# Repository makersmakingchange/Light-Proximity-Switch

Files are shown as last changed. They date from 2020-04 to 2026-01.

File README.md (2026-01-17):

# Light Proximity Switch

> [!IMPORTANT]
2026-Jan-16 Several of the electronic components in this design are no longer available. We are working to determine suitable replacements.

The Light Proximity Switch is an open-source assistive switch that is activated by movement or extremely light contact. It can be activated by waving a hand or limb over the device. This switch has an output cable with a standard 3.5 mm plug and it can be used to control a variety of switch-adapted devices including phones, computers, adapted toys, and gaming consoles.

The Light Proximity Switch is comprised of off-the-shelf electronics, a custom printed circuit board (PCB), and 3D printed parts.

The Light Proximity Switch is open assistive technology (OpenAT). Under the terms of the open source licenses, the device may be built, used, and improved by anyone.

The overall cost of materials for a single build is approximately $35 CAD.

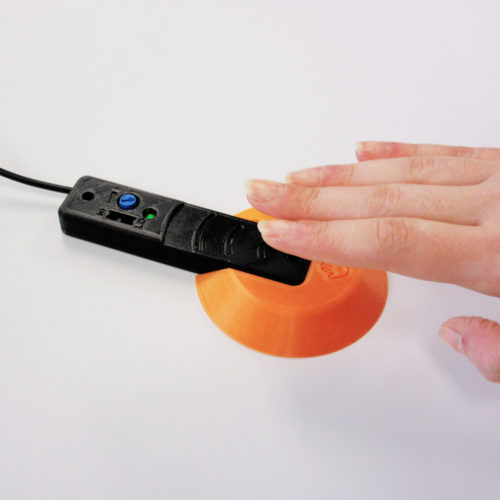
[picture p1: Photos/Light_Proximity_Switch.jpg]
A hand hovering over a black Light Proximity Switch with an orange base.


## More info at

- [Makers Making Change Library Page](https://www.makersmakingchange.com/s/product/light-proximity-switch/01tJR0000006942YAA)

## Usage
Plug the 3.5 mm cable from the switch into the device you want to control. Wave a hand or limb over the sensor to trigger the device (the green LED should light up). 

Fine tune the motion sensitivity by toggling the black switch to "HI" or "LO" then fine tuning using the blue dial.

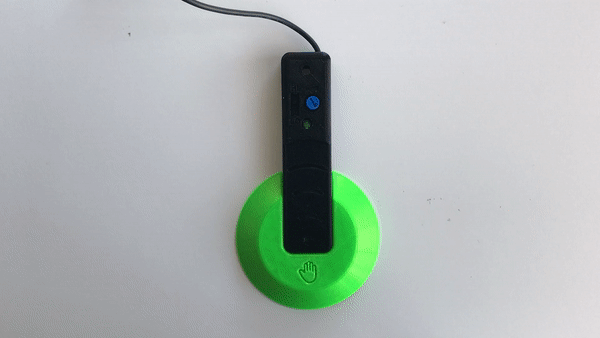
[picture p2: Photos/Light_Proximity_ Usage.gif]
An animation showing the the green light on the Light Proximity Switch activating as a hand is passed over the sensor.


To attach the 3D printed circular base, simply slide the base onto the switch until it clicks into place. This may take a bit of force. The inclined surface of the can make it easier for a user to push their hand up to activate the sensor.

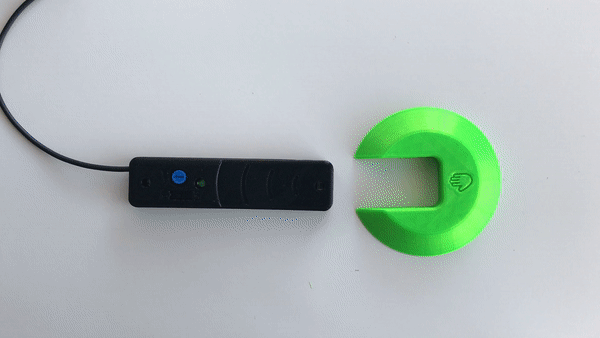
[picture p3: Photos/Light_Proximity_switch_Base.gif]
An animation showing the circular base being clipped on to the Light Proximity Switch.


## How to Obtain the Device
### 1. Do-it-Yourself (DIY) or Do-it-Together (DIT)

This is an open-source assistive technology, so anyone is free to build it. All of the files and instructions required to build the device are contained within this repository. Refer to the documentation below.

### 2. Request a build of this device

You may also submit a build request through the [MMC Library Page](https://www.makersmakingchange.com/s/product/light-proximity-switch/01tJR0000006942YAA) to have a volunteer maker build the device. As the requestor, you are responsible for reimbursing the maker for the cost of materials and any shipping.

### 3. Build this device for someone else

If you have the skills and equipment to build this device, and would like to donate your time to create the device for someone who needs it, visit the [MMC Maker Wanted](https://makersmakingchange.com/maker-wanted/) section.

## Build Instructions

### 1. Read through the Documentation

<!--- The [Assembly Guide](/Documentation/Light_Proxity_Switch_Makery_Guide.pdf) contains all the necessary information to build this device, including tool lists, assembly instructions, and testing. --->
Read through the documentation below.

### 2. Order the Custom Printed Circuit Board (PCB)

This device requires a custom PCB. It will need to be ordered from a PCB fabrication service. The Gerber files can be found in the [PCB Build Files](/Build_Files/PCB_Build_Files/). 

### 3. Order the Off-The-Shelf Components

The [Bill of Materials](/Documentation/Light_Proximity_Switch_BOM.csv) lists all of the parts and components required to build the device. This build also requires a custom PCB.

### 4. Print the 3D Printable components

All of the individual print files can be found in the [/Build_Files/3D_Printing_Files](/Build_Files/3D_Printing/) folder.

### 5. Assemble the Light Proximity Switch

Reference the [Assembly Guide](/Documentation/Light_Proxity_Switch_Assembly_Guide.pdf) for the tools and steps required to build each portion.

## How to improve this Device Design
As open assistive technology, you are welcomed and encouraged to improve upon the design. 

## Files
### Documentation
| Document             | Version | Link |
|----------------------|---------|------|
| Design Rationale     | n/a     | WIP   |
| Bill of Materials    | 1.0     |  [Light Proximity Switch BOM](/Documentation/Light_Proximity_Switch_BOM.csv)  |
| Tool List | 1.0 | [Light Proximity Switch Tools List](/Documentation/Light_Proximity_Switch_Tools_List.pdf)|
| Assembly Guide       | 1.0     | [Light Proximity Switch Assembly Guide](/Documentation/Light_Proxity_Switch_Assembly_Guide.pdf) |
| QC Quide | 1.0 | [Light Proximity Switch QC Guide](/Documentation/Light_Proximity_Switch_QC_Guide.pdf)|
| Troubleshooting Guide | 1.0 | [Light Proximity Switch Troubleshooting Guide](/Documentation/Light_Proximity_Switch_Troubleshooting_Guide.pdf)|
| Delivery Checklist | 1.0 | [Light Proximity Delivery Checklist](/Documentation/Light_Proximity_Switch_Delivery_Checklist.pdf)|
| User Guide           | 1.0     | [Light Proximity Switch User Guide](/Documentation/Light_Proximity_Switch_User_Guide.pdf) |
| Changelog            | n/a     | -     |

### Design Files
<!---
DESIGN FILES
--->
 - [CAD Files](/Design_Files/CAD_Design_Files)
 - [PCB Design Files](/Design_Files/PCB_Design_Files/)

### Build Files
 - [3D Printing Files](/Build_Files/3D_Printing_Files)
 - [PCB Build Files](/Build_Files/PCB_Build_Files)

## License
Copyright (c) 2019-2026 Neil Squire / Makers Making Change.

This repository describes Open Hardware:
 - Everything needed or used to design, make, test, or prepare the Light Proximity Switch is licensed under the [CERN 2.0 Weakly Reciprocal license (CERN-OHL-W v2) or later](https://cern.ch/cern-ohl ) .
 - Accompanying material such as instruction manuals, videos, and other copyrightable works that are useful but not necessary to design, make, test, or prepare the Light Proximity Switch are published under a [Creative Commons Attribution-ShareAlike 4.0 license (CC BY-SA 4.0)](https://creativecommons.org/licenses/by-sa/4.0/) .

You may redistribute and modify this documentation and make products using it under the terms of the [CERN-OHL-W v2](https://cern.ch/cern-ohl).
This documentation is distributed WITHOUT ANY EXPRESS OR IMPLIED WARRANTY, INCLUDING OF MERCHANTABILITY, SATISFACTORY QUALITY AND FITNESS FOR A PARTICULAR PURPOSE.
Please see the CERN-OHL-W v2 for applicable conditions.

Source Location: https://github.com/makersmakingchange/Light-Proximity-Switch

## Attribution
The Light Proximity Switch is an original design by Neil Squire / Maker Making Change Program.

### Contributors
  - Derrick Andrews, Neil Squire Society / Makers Making Change.
  - Jake McIvor, Neil Squire Society / Makers Making Change.
  - Kristina Mok, Neil Squire Society / Makers Making Change.

<!-- ABOUT MMC START -->
## About Makers Making Change
[Makers Making Change Logo](https://www.makersmakingchange.com/)

Makers Making Change is a program of [Neil Squire](https://www.neilsquire.ca/), a Canadian non-profit that uses technology, knowledge, and passion to empower people with disabilities.

Makers Making Change leverages the capacity of community based Makers, Disability Professionals and Volunteers to develop and deliver affordable Open Source Assistive Technologies.

 - Website: [www.MakersMakingChange.com](https://www.makersmakingchange.com/)
 - GitHub: [makersmakingchange](https://github.com/makersmakingchange)
 - Bluesky: [@makersmakingchange.bsky.social](https://bsky.app/profile/makersmakingchange.bsky.social)
 - Instagram: [@makersmakingchange](https://www.instagram.com/makersmakingchange)
 - Facebook: [makersmakechange](https://www.facebook.com/makersmakechange)
 - LinkedIn: [Neil Squire Society](https://www.linkedin.com/company/neil-squire-society/)
 - Thingiverse: [makersmakingchange](https://www.thingiverse.com/makersmakingchange/about)
 - Printables: [MakersMakingChange](https://www.printables.com/@MakersMakingChange)

### Contact Us
For technical questions, to get involved, or to share your experience we encourage you to [visit our website](https://www.makersmakingchange.com/) or [contact us](https://www.makersmakingchange.com/s/contact).
<!-- ABOUT MMC END -->

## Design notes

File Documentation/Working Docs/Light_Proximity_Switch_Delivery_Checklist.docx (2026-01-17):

## Maker To Do

Light Proximity Switch - Device Delivery Checklist

☐ Build the Light Proximity Switch

☐ 3D print the switch base

# Items for the User

☐ Light Proximity Switch

☐ Light Proximity Switch Base

☐ Light Proximity Switch: User Guide

Neil Squire, 2020 © 2020 by Neil Squire. Proximity Switch Delivery Checklist is made available under a Creative Commons Attribution-ShareAlike 4.0 License (International): http://creativecommons.org/licenses/by-sa/4.0

Version 1.0 | March 2020 www.MakersMakingChange.com

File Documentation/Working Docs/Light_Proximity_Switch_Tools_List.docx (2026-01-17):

Proximity Switch: Tool List

# Tools

- Soldering iron
- Solder
- Flush cutters
- Wire strippers
- Needle nose pliers
- Mini Philips screwdriver
- De-soldering tool
- Tape
- Clamp

Neil Squire, 2020 © 2020 by Neil Squire. Proximity Switch Tool List is made available under a Creative Commons Attribution-ShareAlike 4.0 License (International): http://creativecommons.org/licenses/by-sa/4.0

Version 1.0 | February 2020 www.MakersMakingChange.com

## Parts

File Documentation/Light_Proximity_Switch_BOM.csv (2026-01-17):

Qty | Component | Component name | Supplier | Manufacturer | MPN | Digi-Key Part Number | Unit Cost (CAD) | Build Cost (CAD) | Link
1 | IC1 | IC OPAMP GP 1 CIRCUIT 8DIP | DigiKey | Microchip Technology | MCP6231-E/P | MCP6231-E/P-ND | $0.69 | $0.69 | https://www.digikey.ca/en/products/detail/microchip-technology/MCP6231-E-P/716239?s=N4IgTCBcDaILIGEAKA2MBmAjAWgKIHolsA5AERAF0BfIA
2 | D1,D3 | SENSOR PHOTODIODE 850NM 2DIP | DigiKey | OSRAM | BPW34 | 475-1070-ND | $1.63 | $3.26 | https://www.digikey.ca/product-detail/en/osram-opto-semiconductors-inc/BPW34/475-1070-ND/607274
1 | D2 | Schottky diode 1N5817 | DigiKey | STMicroelectronics | 1N5817 | 497-4547-1-ND | $0.33 | $0.33 | https://www.digikey.ca/en/products/detail/stmicroelectronics/1N5817/770963
1 | LED1 | LED GREEN CLEAR 5MM ROUND | DigiKey | Cree LED | C566D-GFF-CY14Q7S1 | C566D-GFF-CY14Q7S1-ND | $0.43 | $0.43 | https://www.digikey.ca/en/products/detail/cree-led/C566D-GFF-CY14Q7S1/4793750
1 | C1 | CAP CER 10000PF 50V Z5U RADIAL | DigiKey | KEMET | C315C103M5U5TA7301 | 399-13973-1-ND | $0.40 | $0.40 | https://www.digikey.ca/product-detail/en/kemet/C315C103M5U5TA7301/399-13973-1-ND/6562544
2 | C2,C5 | CAP CER 33PF 50V X7R RADIAL | DigiKey | KEMET | C315C330K2G5TA7301 | 399-13940-1-ND | $0.54 | $1.08 | https://www.digikey.ca/product-detail/en/kemet/C315C330K2G5TA7301/399-13940-1-ND/6562533
1 | C3 | CAP CER 10PF 50V C0G/NP0 RADIAL | DigiKey | Vishay Siliconix | K100J15C0GF5TL2 | BC1001CT-ND | $0.35 | $0.35 | https://www.digikey.ca/product-detail/en/vishay-bc-components/K100J15C0GF5TL2/BC1001CT-ND/286623
1 | C4 | CAP CER 1UF 25V X7R RADIAL | DigiKey | KEMET | C315C105K3R5TA | 399-9714-ND | $1.32 | $1.32 | https://www.digikey.ca/en/products/detail/kemet/C315C105K3R5TA/3726118
1 | R1 | TRIMMER 100K OHM 0.5W PC PIN TOP | DigiKey | Bourns Inc. | 3386P-1-104TLF | 3386P-104TLF-ND | $3.39 | $3.39 | https://www.digikey.ca/product-detail/en/bourns-inc/3386P-1-104TLF/3386P-104TLF-ND/1232548
1 | R3 | 200K Resistor | DigiKey | Yageo | CFR-25JB-52-200K | 200KQBK-ND | $0.15 | $0.15 | https://www.digikey.ca/product-detail/en/yageo/CFR-25JB-52-200K/200KQBK-ND/711
1 | R2 | RES 10K OHM 1/4W 5% AXIAL | DigiKey | Yageo | CFR-25JB-52-10K | 10KQBK-ND | $0.15 | $0.15 | https://www.digikey.ca/product-detail/en/yageo/CFR-25JB-52-10K/10KQBK-ND/338
1 | B1 | CR2032 battery holder | DigiKey | Memory Protection Devices | BU2032SM-BT-GTR | BU2032SM-FH-GCT-ND | $1.88 | $1.88 | https://www.digikey.ca/en/products/detail/mpd-memory-protection-devices/BU2032SM-BT-GTR/2439521
1 | S1 | SWITCH SLIDE SPDT 200MA 30V | DigiKey | E-Switch | EG1218 | EG1903-ND | $1.21 | $1.21 | https://www.digikey.ca/product-detail/en/e-switch/EG1218/EG1903-ND/101726
1 | 3.5mm Cable | CBL ASSY 3.5MM SLIM 6' MONO BLK | DigiKey | Tensility International Corp | 10-00344 | 839-1039-ND | $3.49 | $3.49 | https://www.digikey.ca/product-detail/en/tensility-international-corp/10-00344/839-1039-ND/2350247
1 | Cable Tie | Cable Tie, Nylon, 71 mm long, 1.8 mm wide | Digikey | Panduit | PLT.6SM-C | PLT.6SM-C | $0.32 | $0.32 | https://www.digikey.ca/en/products/detail/panduit-corp/PLT-6SM-C/280029
2 | Screws | M2X8mm screw | DigiKey | APM Hexseal | RM2X8MM 2701 | 335-1155-ND | $1.14 | $2.28 | https://www.digikey.ca/product-detail/en/apm-hexseal/RM2X8MM-2701/335-1155-ND/612919
2 | Q1,Q2 | MOSFET N-CH 100V 1A 4-DIP | Amazon |  | IRLD110PBF |  | $1.28 | $2.55 | https://www.amazon.ca/10PCS-IRLD110-DIP4-IRLD110PBF-DIP-4/dp/B0DSSJTPH8
1 | CR2032 | CR2032 3V Battery | Amazon | AmazonBasics | CR2032 |  | $0.73 | $0.73 | https://www.amazon.ca/AmazonBasics-Lithium-CR2032-Batteries-10-Pack/dp/B07RXJ4S7Z
 |  |  |  |  |  | Total Electronics Cost | $24.01 | $24.01

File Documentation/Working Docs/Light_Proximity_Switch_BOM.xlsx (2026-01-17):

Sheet: Electronics
Qty | Component | Component name | Supplier | Manufacturer | MPN | Digi-Key Part Number | Unit Cost (CAD) | Build Cost (CAD) | Link
1 | IC1 | IC OPAMP GP 1 CIRCUIT 8DIP | DigiKey | Microchip Technology | MCP6231-E/P | MCP6231-E/P-ND | $0.69 | $0.69 | https://www.digikey.ca/en/products/detail/microchip-technology/MCP6231-E-P/716239?s=N4IgTCBcDaILIGEAKA2MBmAjAWgKIHolsA5AERAF0BfIA
2 | D1,D3 | SENSOR PHOTODIODE 850NM 2DIP | DigiKey | OSRAM | BPW34 | 475-1070-ND | $1.63 | $3.26 | https://www.digikey.ca/product-detail/en/osram-opto-semiconductors-inc/BPW34/475-1070-ND/607274
1 | D2 | Schottky diode 1N5817 | DigiKey | STMicroelectronics | 1N5817 | 497-4547-1-ND | $0.33 | $0.33 | https://www.digikey.ca/en/products/detail/stmicroelectronics/1N5817/770963
1 | LED1 | LED GREEN CLEAR 5MM ROUND | DigiKey | Cree LED | C566D-GFF-CY14Q7S1 | C566D-GFF-CY14Q7S1-ND | $0.43 | $0.43 | https://www.digikey.ca/en/products/detail/cree-led/C566D-GFF-CY14Q7S1/4793750
1 | C1 | CAP CER 10000PF 50V Z5U RADIAL | DigiKey | KEMET | C315C103M5U5TA7301 | 399-13973-1-ND | $0.40 | $0.40 | https://www.digikey.ca/product-detail/en/kemet/C315C103M5U5TA7301/399-13973-1-ND/6562544
2 | C2,C5 | CAP CER 33PF 50V X7R RADIAL | DigiKey | KEMET | C315C330K2G5TA7301 | 399-13940-1-ND | $0.54 | $1.08 | https://www.digikey.ca/product-detail/en/kemet/C315C330K2G5TA7301/399-13940-1-ND/6562533
1 | C3 | CAP CER 10PF 50V C0G/NP0 RADIAL | DigiKey | Vishay Siliconix | K100J15C0GF5TL2 | BC1001CT-ND | $0.35 | $0.35 | https://www.digikey.ca/product-detail/en/vishay-bc-components/K100J15C0GF5TL2/BC1001CT-ND/286623
1 | C4 | CAP CER 1UF 25V X7R RADIAL | DigiKey | KEMET | C315C105K3R5TA | 399-9714-ND | $1.32 | $1.32 | https://www.digikey.ca/en/products/detail/kemet/C315C105K3R5TA/3726118
1 | R1 | TRIMMER 100K OHM 0.5W PC PIN TOP | DigiKey | Bourns Inc. | 3386P-1-104TLF | 3386P-104TLF-ND | $3.39 | $3.39 | https://www.digikey.ca/product-detail/en/bourns-inc/3386P-1-104TLF/3386P-104TLF-ND/1232548
1 | R3 | 200K Resistor | DigiKey | Yageo | CFR-25JB-52-200K | 200KQBK-ND | $0.15 | $0.15 | https://www.digikey.ca/product-detail/en/yageo/CFR-25JB-52-200K/200KQBK-ND/711
1 | R2 | RES 10K OHM 1/4W 5% AXIAL | DigiKey | Yageo | CFR-25JB-52-10K | 10KQBK-ND | $0.15 | $0.15 | https://www.digikey.ca/product-detail/en/yageo/CFR-25JB-52-10K/10KQBK-ND/338
1 | B1 | CR2032 battery holder | DigiKey | Memory Protection Devices | BU2032SM-BT-GTR | BU2032SM-FH-GCT-ND | $1.88 | $1.88 | https://www.digikey.ca/en/products/detail/mpd-memory-protection-devices/BU2032SM-BT-GTR/2439521
1 | S1 | SWITCH SLIDE SPDT 200MA 30V | DigiKey | E-Switch | EG1218 | EG1903-ND | $1.21 | $1.21 | https://www.digikey.ca/product-detail/en/e-switch/EG1218/EG1903-ND/101726
1 | 3.5mm Cable | CBL ASSY 3.5MM SLIM 6' MONO BLK | DigiKey | Tensility International Corp | 10-00344 | 839-1039-ND | $3.49 | $3.49 | https://www.digikey.ca/product-detail/en/tensility-international-corp/10-00344/839-1039-ND/2350247
1 | Cable Tie | Cable Tie, Nylon, 71 mm long, 1.8 mm wide | Digikey | Panduit | PLT.6SM-C | PLT.6SM-C | $0.32 | $0.32 | https://www.digikey.ca/en/products/detail/panduit-corp/PLT-6SM-C/280029
2 | Screws | M2X8mm screw | DigiKey | APM Hexseal | RM2X8MM 2701 | 335-1155-ND | $1.14 | $2.28 | https://www.digikey.ca/product-detail/en/apm-hexseal/RM2X8MM-2701/335-1155-ND/612919
2 | Q1,Q2 | MOSFET N-CH 100V 1A 4-DIP | Amazon |  | IRLD110PBF |  | $1.28 | $2.55 | https://www.amazon.ca/10PCS-IRLD110-DIP4-IRLD110PBF-DIP-4/dp/B0DSSJTPH8
1 | CR2032 | CR2032 3V Battery | Amazon | AmazonBasics | CR2032 |  | $0.73 | $0.73 | https://www.amazon.ca/AmazonBasics-Lithium-CR2032-Batteries-10-Pack/dp/B07RXJ4S7Z
 |  |  |  |  |  | Total Electronics Cost | $24.01 | $24.01

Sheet: PCB
Qty | Manufacturer | Fabrication Time | Delivery option | Delivery Cost (USD) | Fabrication Cost(USD) | Tax (USD) | Total Cost (USD) | Total Cost (CAD) | Unit Cost (CAD) | Link
5 | JLCPCB | 1-2 days for green and 3-4 for other colors | *S.F Express( 3-5 business days) | $24.82 | $2 | $15.00 | $41.82 | $55.62 | $11.12 | https://jlcpcb.com
5 | JLCPCB | 1-2 days for green and 3-4 for other colors | *DHL Express ( 3-5 business days) | $20.22 | $2 | $15.00 | $37.22 | $49.50 | $9.90 | https://jlcpcb.com
5 | JLCPCB | 1-2 days for green and 3-4 for other colors | Registered Air Mail (15-20 business days) | $9.47 | $2 | $0.00 | $11.47 | $15.26 | $3.05 | https://jlcpcb.com
10 | JLCPCB | 3-4 days for green and 5-6 for other colors | *S.F Express( 3-5 business days) | $24.82 | $5 | $15.00 | $44.82 | $59.61 | $5.96 | https://jlcpcb.com
10 | JLCPCB | 3-4 days for green and 5-6 for other colors | *DHL Express ( 3-5 business days) | $20.22 | $5 | $15.00 | $40.22 | $53.49 | $5.35 | https://jlcpcb.com
10 | JLCPCB | 3-4 days for green and 5-6 for other colors | Registered Air Mail (15-20 business days) | $9.47 | $5 | $0.00 | $14.47 | $19.25 | $1.92 | https://jlcpcb.com
50 | JLCPCB | 5-6 days for green | *S.F Express( 3-5 business days) | $24.82 | $12.80 | $15.00 | $52.62 | $69.98 | $1.40 | https://jlcpcb.com
50 | JLCPCB | 7-8 for other colors | *S.F Express( 3-5 business days) | $24.82 | $27.30 | $15.00 | $67.12 | $89.27 | $1.79 | https://jlcpcb.com
50 | JLCPCB | 5-6 days for green | *DHL Express ( 3-5 business days) | $20.22 | $12.80 | $15.00 | $48.02 | $63.87 | $1.28 | https://jlcpcb.com
50 | JLCPCB | 7-8 for other colors | *DHL Express ( 3-5 business days) | $20.22 | $27.30 | $15.00 | $62.52 | $83.15 | $1.66 | https://jlcpcb.com
50 | JLCPCB | 5-6 days for green | Registered Air Mail (15-20 business days) | $13.29 | $12.80 | $0.00 | $26.09 | $34.70 | $0.69 | https://jlcpcb.com
50 | JLCPCB | 7-8 for other colors | Registered Air Mail (15-20 business days) | $13.29 | $27.30 | $0.00 | $40.59 | $53.98 | $1.08 | https://jlcpcb.com
5 | PCBWay | 1-2 days for green and 3-4 for other colors | *DHL Express ( 3-5 business days) | $21 | $5 | $15.00 | $41.00 | $54.53 | $10.91 | https://www.pcbway.com/
5 | PCBWay | 1-2 days for green and 3-4 for other colors | China Post ( 10-15 business days) | $7 | $5 | $0.00 | $12.00 | $15.96 | $3.19 | https://www.pcbway.com/
5 | PCBWay | 1-2 days for green and 3-4 for other colors | E-packet ( 25-40 business days) | $6 | $5 | $0.00 | $11.00 | $14.63 | $2.93 | https://www.pcbway.com/
5 | PCBWay | 1-2 days for green and 3-4 for other colors | *FedEx IE (6-10 business days) | $26 | $5 | $15.00 | $46.00 | $61.18 | $12.24 | https://www.pcbway.com/
10 | PCBWay | 1-2 days for green and 3-4 for other colors | *DHL Express ( 3-5 business days) | $21 | $5 | $15.00 | $41.00 | $54.53 | $5.45 | https://www.pcbway.com/
10 | PCBWay | 1-2 days for green and 3-4 for other colors | E-packet ( 10-15 business days) | $7 | $5 | $0.00 | $12.00 | $15.96 | $1.60 | https://www.pcbway.com/
10 | PCBWay | 1-2 days for green and 3-4 for other colors | China Post ( 25-40 business days) | $7 | $5 | $0.00 | $12.00 | $15.96 | $1.60 | https://www.pcbway.com/
10 | PCBWay | 1-2 days for green and 3-4 for other colors | *FedEx IE (6-10 business days) | $26 | $5 | $15.00 | $46.00 | $61.18 | $6.12 | https://www.pcbway.com/
50 | PCBWay | 1-2 days for green and 3-4 for other colors | *DHL Express ( 3-5 business days) | $28 | $27 | $15.00 | $70.00 | $93.10 | $1.86 | https://www.pcbway.com/
50 | PCBWay | 1-2 days for green and 3-4 for other colors | E-packet ( 10-15 business days) | $11 | $27 | $0.00 | $38.00 | $50.54 | $1.01 | https://www.pcbway.com/
50 | PCBWay | 1-2 days for green and 3-4 for other colors | China Post ( 25-40 business days) | $11 | $27 | $0.00 | $38.00 | $50.54 | $1.01 | https://www.pcbway.com/
50 | PCBWay | 1-2 days for green and 3-4 for other colors | *FedEx IE (6-10 business days) | $26 | $27 | $15.00 | $68.00 | $90.44 | $1.81 | https://www.pcbway.com/
5 | SeeedStudio Fusion | 3-4 for all colors (2 more days for Matte Black ) | *DHL ( 1-3 business days) | $23.8 | $4.9 | $15.00 | $43.70 | $58.12 | $11.62 | https://www.seeedstudio.com
5 | SeeedStudio Fusion | 3-4 for all colors (2 more days for Matte Black ) | *FedEx (4-8 business days) | $24.55 | $4.9 | $15.00 | $44.45 | $59.12 | $11.82 | https://www.seeedstudio.com
10 | SeeedStudio Fusion | 3-4 for all colors (2 more days for Matte Black ) | *DHL ( 1-3 business days) | $23.8 | $4.9 | $15.00 | $43.70 | $58.12 | $5.81 | https://www.seeedstudio.com
10 | SeeedStudio Fusion | 3-4 for all colors (2 more days for Matte Black ) | *FedEx (4-8 business days) | $24.55 | $4.9 | $15.00 | $44.45 | $59.12 | $5.91 | https://www.seeedstudio.com
50 | SeeedStudio Fusion | 3-4 for all colors (2 more days for Matte Black ) | *DHL ( 1-3 business days) | $26.70 | $26.36 | $15.00 | $68.06 | $90.52 | $1.81 | https://www.seeedstudio.com
50 | SeeedStudio Fusion | 3-4 for all colors (2 more days for Matte Black ) | *FedEx (4-8 business days) | $28.54 | $26.36 | $15.00 | $69.90 | $92.97 | $1.86 | https://www.seeedstudio.com
100 | SeeedStudio Fusion | 3-4 for all colors (2 more days for Matte Black ) | *DHL ( 1-3 business days) | $29.60 | $39.13 | $15.00 | $83.73 | $111.36 | $1.11 | https://www.seeedstudio.com
100 | SeeedStudio Fusion | 3-4 for all colors (2 more days for Matte Black ) | *FedEx (4-8 business days) | $32.50 | $39.13 | $15.00 | $86.63 | $115.22 | $1.15 | https://www.seeedstudio.com
3 | OSH Park | Prototype (9-12 business days) [1] |  |  | $15.85 |  |  |  |  | https://oshpark.com/
6 | OSH Park | Prototype (9-12 business days) [1] |  |  | $31.7 |  |  |  |  | https://oshpark.com/
9 | OSH Park | Prototype (9-12 business days) [1] |  |  | $47.55 |  |  |  |  | https://oshpark.com/
12 | OSH Park | Prototype (9-12 business days) [1] |  |  | $63.40 |  |  |  |  | https://oshpark.com/
21 | OSH Park | Prototype (9-12 business days) [1] |  |  | $110.95 |  |  |  |  | https://oshpark.com/
51 | OSH Park | Prototype (9-12 business days) [1] |  |  | $269.45 |  |  |  |  | https://oshpark.com/
102 | OSH Park | Prototype (9-12 business days) [1] |  |  | $538.90 |  |  |  |  | https://oshpark.com/
3 | OSH Park | Super Swift (4-5 business days) [2] |  |  | $31.70 |  |  |  |  | https://oshpark.com/
6 | OSH Park | Super Swift (4-5 business days) [2] |  |  | $63.40 |  |  |  |  | https://oshpark.com/
9 | OSH Park | Super Swift (4-5 business days) [2] |  |  | $95.1 |  |  |  |  | https://oshpark.com/
12 | OSH Park | Super Swift (4-5 business days) [2] |  |  | $126.80 |  |  |  |  | https://oshpark.com/
21 | OSH Park | Super Swift (4-5 business days) [2] |  |  | $221.90 |  |  |  |  | https://oshpark.com/
51 | OSH Park | Super Swift (4-5 business days) [2] |  |  | $538.90 |  |  |  |  | https://oshpark.com/
102 | OSH Park | Super Swift (4-5 business days) [2] |  |  | $1077.80 |  |  |  |  | https://oshpark.com/
40 | OSH Park | Bulk Order (9-14 business days) [3] |  |  | $126.80 |  |  |  |  | https://oshpark.com/
50 | OSH Park | Bulk Order (9-14 business days) [3] |  |  | $158.50 |  |  |  |  | https://oshpark.com/
100 | OSH Park | Bulk Order (9-14 business days) [3] | Standard First Class Mail(5-21 business days) | $0 | $317 | $0 | $317.00 | $421.61 | $4.22 | https://oshpark.com/
100 | OSH Park | Bulk Order (9-14 business days) [3] | UPS Saver (1 business day) | $33 | $317 | $15.00 | $365.00 | $485.45 | $4.85
 | 1 | $5 per square inch, which includes three copies of your design
 | 2 | $10 per square inch, which includes three copies of your design
 | 3 | $1 per square inch, 100 square inch minimum.

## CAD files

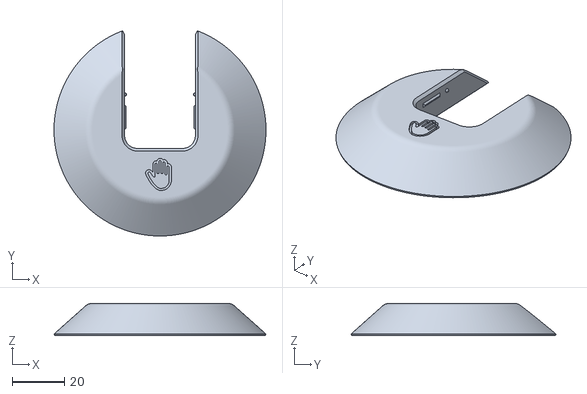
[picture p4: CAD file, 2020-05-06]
Build_Files/3D_Printing_Files/Light_Proximity_Switch_Base.stl
81.5 x 78.8 x 12.5

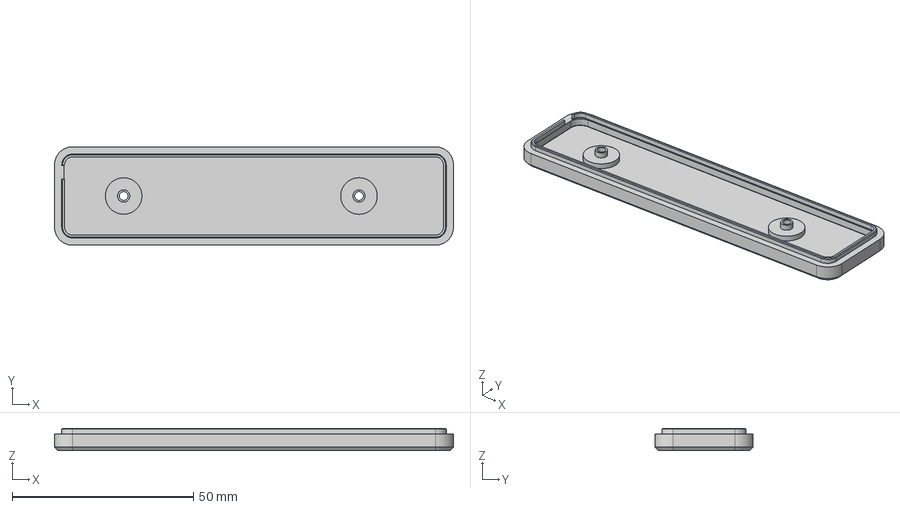
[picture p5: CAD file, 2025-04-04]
Design_Files/CAD_Design_Files/Light_Proximity_Switch_Bottom_Case.step
110.2 x 27.2 x 6.17 mm

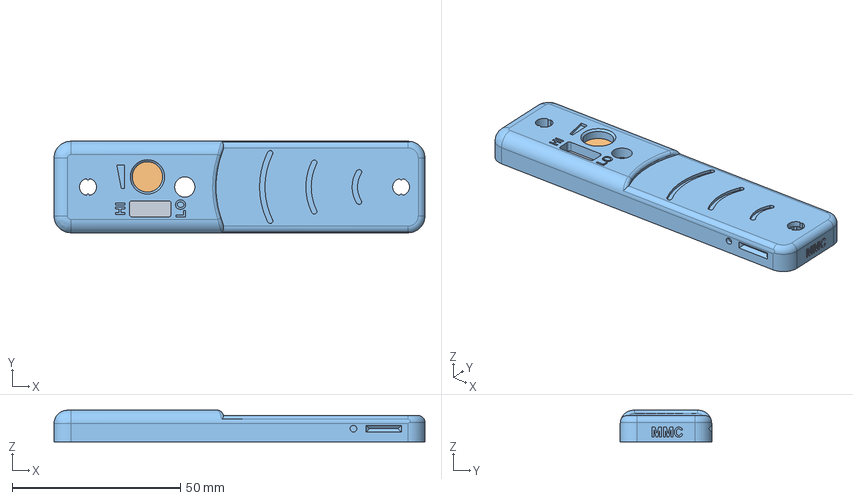
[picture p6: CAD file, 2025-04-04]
Design_Files/CAD_Design_Files/Light_Proximity_Switch_Top_Case.step
110.2 x 27.2 x 9.40 mm

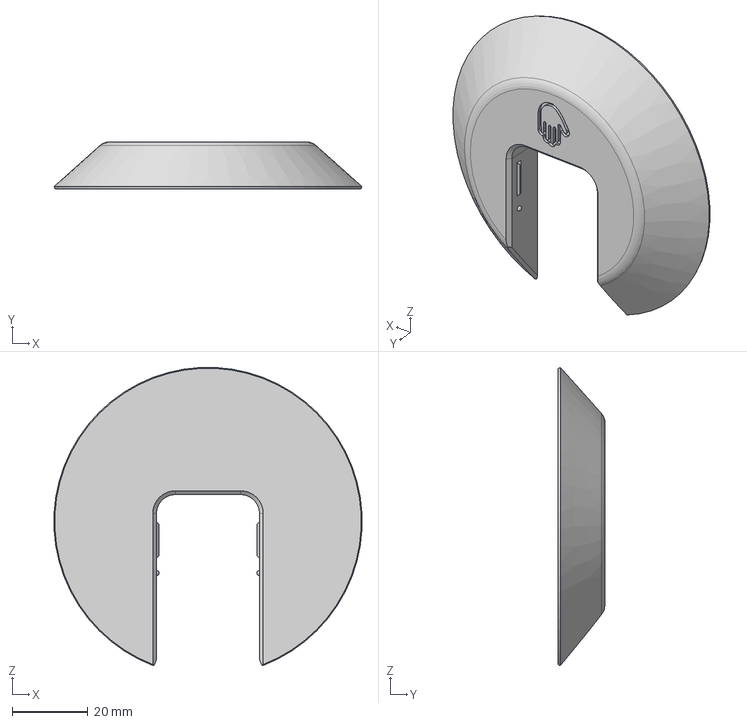
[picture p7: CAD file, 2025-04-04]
Design_Files/CAD_Design_Files/Light_Proximity_Switch_Base.step
81.4 x 12.5 x 78.8 mm

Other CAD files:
Build_Files/3D_Printing_Files/Light_Proximity_Switch_Bottom_Case.stl
Build_Files/3D_Printing_Files/Light_Proximity_Switch_Top_Case.stl

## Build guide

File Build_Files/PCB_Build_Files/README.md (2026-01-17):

# Custom PCB 
## Schematic
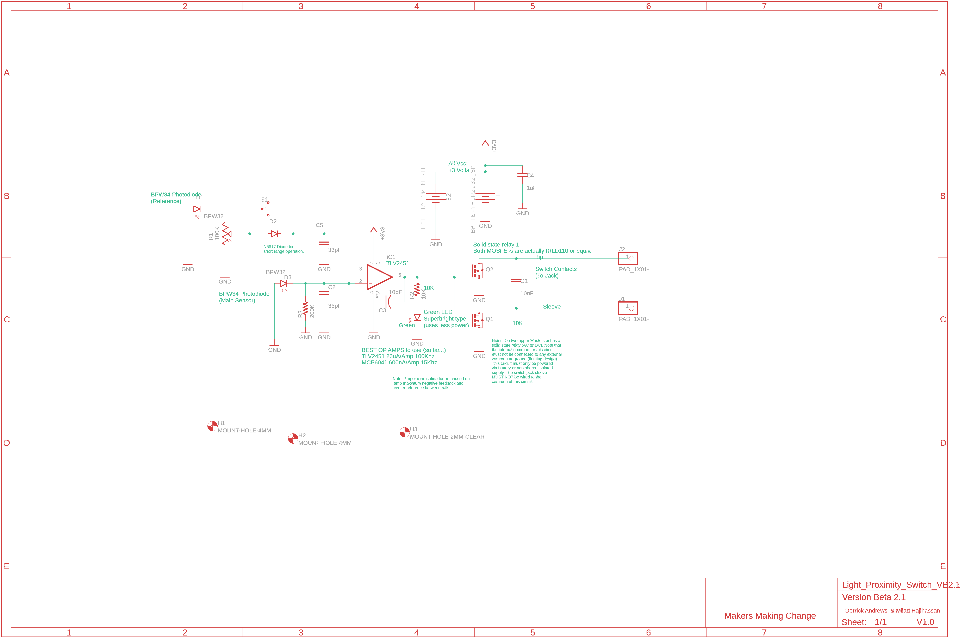
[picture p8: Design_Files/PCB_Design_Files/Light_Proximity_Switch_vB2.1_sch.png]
Image of circuit schematic Schematic


## PCB
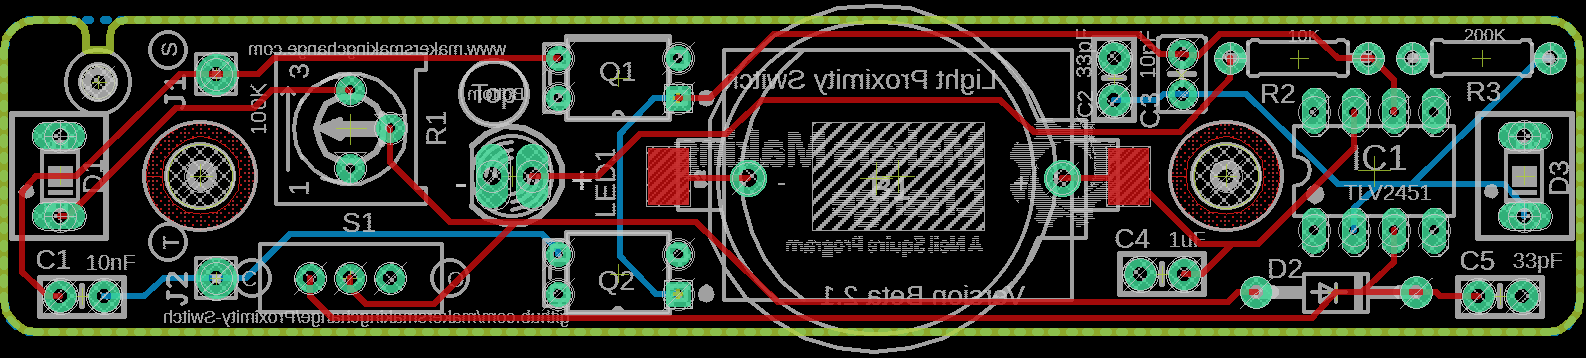
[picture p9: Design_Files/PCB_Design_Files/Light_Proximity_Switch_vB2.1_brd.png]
Image of PCB Board Board


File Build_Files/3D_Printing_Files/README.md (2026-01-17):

# 3D Print Files
| File                               | Resolution | Infill | Support |
|------------------------------------|------------|--------|---------|
| [Light_Proximity_Switch_Base](/Light_Proximity_Switch_Base.stl)        | 0.2 mm     | 20%    | No      |
| [Light_Proximity_Switch_Bottom_Case](/Light_Proximity_Switch_Bottom_Case.stl) | 0.2 mm     | 20%    | No      |
| [Light_Proximity_Switch_Top_Case](/Light_Proximity_Switch_Top_Case.stl)    | 0.2 mm     | 20%    | No      |

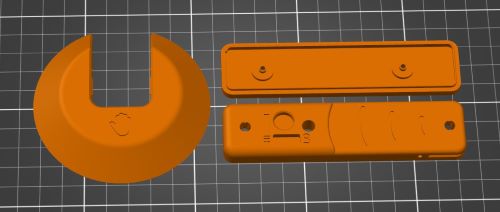
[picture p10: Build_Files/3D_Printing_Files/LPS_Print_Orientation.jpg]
Screenshot of print orientation


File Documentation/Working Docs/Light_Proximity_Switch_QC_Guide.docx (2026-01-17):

Proximity Switch: QC Guide

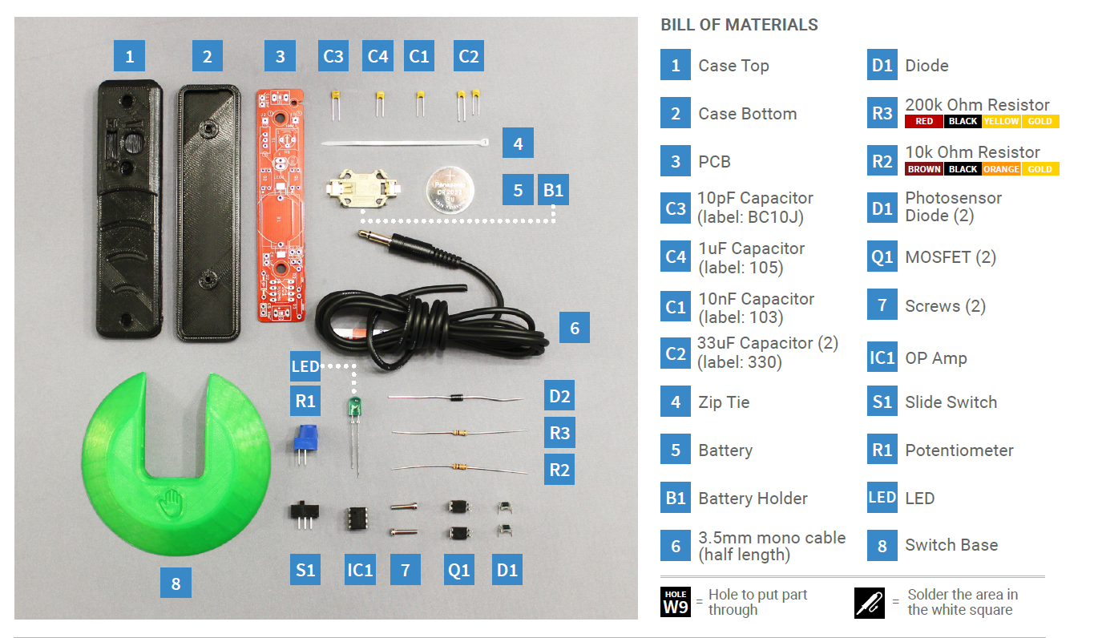
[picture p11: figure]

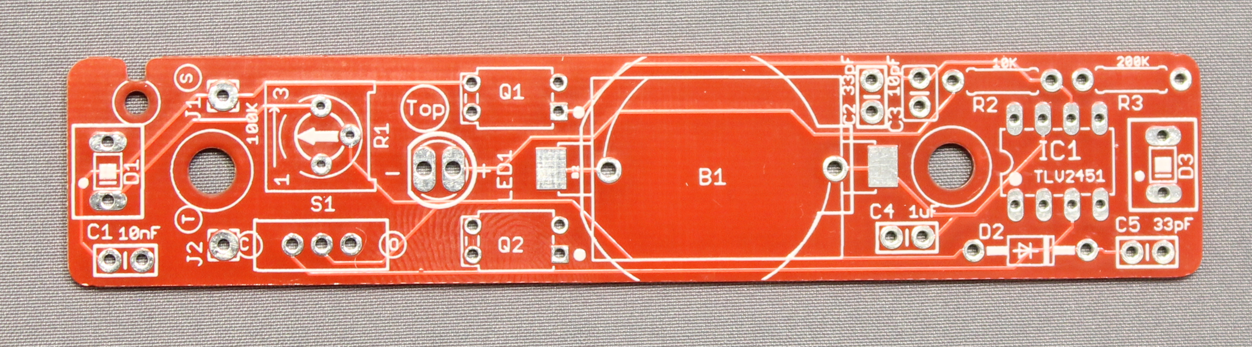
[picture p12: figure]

| Solder on the correct PCB side All component will be inserted on the PCB side that says “Top” and soldered on the side marked “Bottom”.

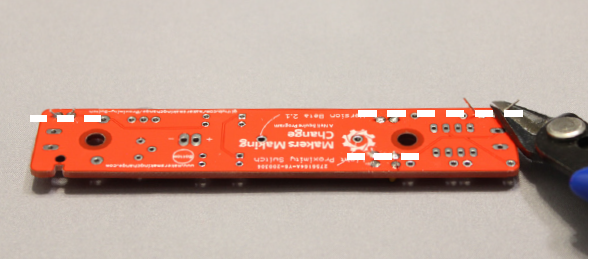
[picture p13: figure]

| Trim all excess leads There is limited space between the bottom of the PCB and the bottom case. Make sure all leads are trimmed after soldering so it fits in the case.

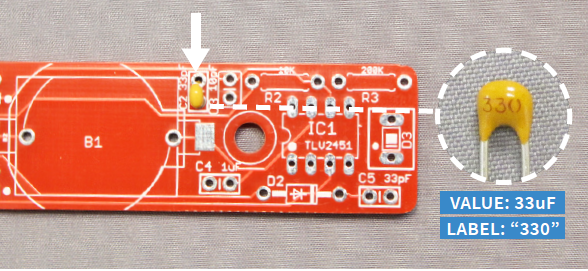
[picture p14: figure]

| Capacitors Capacitors may look similar so look at the printed labelling to differentiate them.

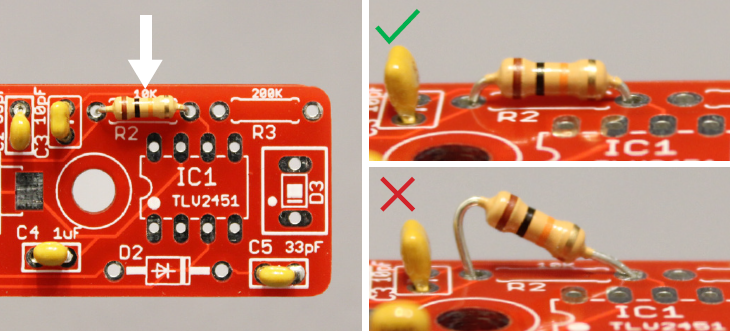
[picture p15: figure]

| Ensure components are inserted flush to the board Components not soldered flush to the board may interfere with the case. A good tip is to solder one lead first, check to see if part is flush, and continue soldering.

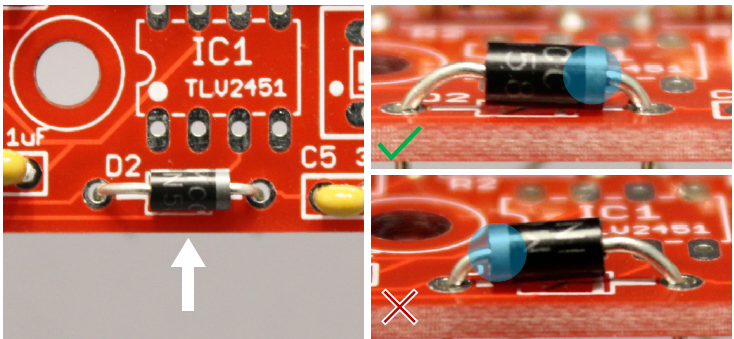
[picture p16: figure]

| Diode Insert the diode with the silver band towards the C5 marking.

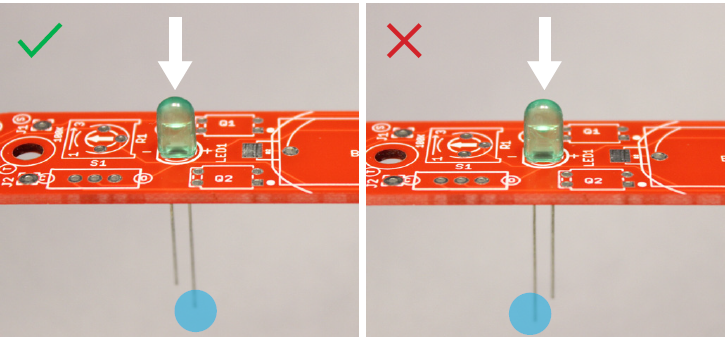
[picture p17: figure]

| LED Insert the LED with the longer lead towards the centre of the PCB.

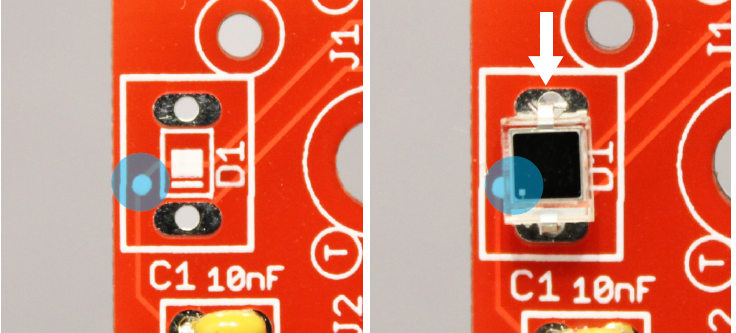
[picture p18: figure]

| White dot Several components have white dots on the top. Align the white dot on the component with the white dot on the PCB.

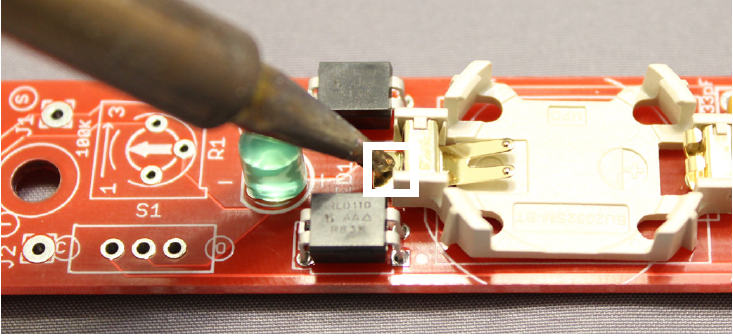
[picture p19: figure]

| Soldering the battery holder Be careful of the soldering iron when soldering the battery holder to the PCB as the heat may damage surrounding components.

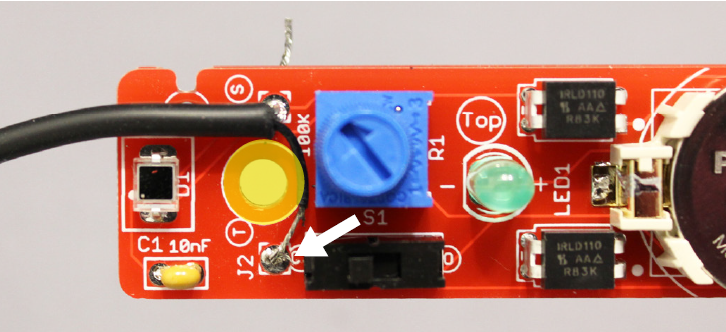
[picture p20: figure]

| Mono cable When inserting and soldering the mono cable to the PCB, ensure enough clearance around the highlighted yellow circle.

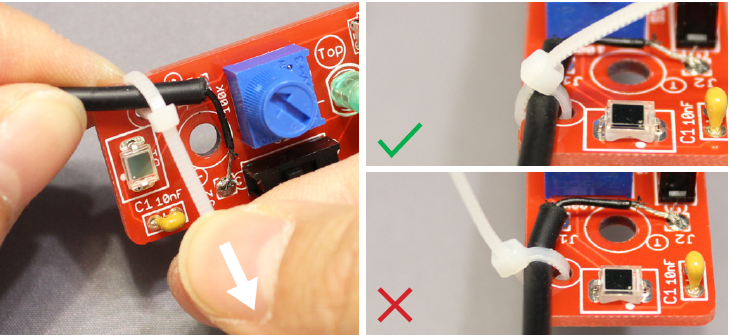
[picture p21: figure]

| Zip tie Cinch the zip tie in the depicted manner or else the knot will interfere with the case.

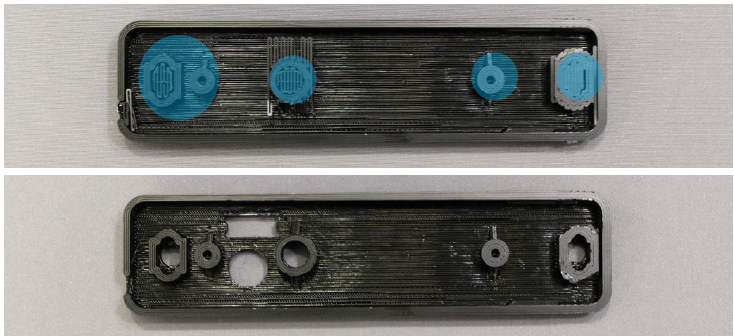
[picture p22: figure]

| Support Material Remove all the support material from the top case.

Neil Squire, 2020 © 2020 by Neil Squire. Proximity Switch QC Guide is made available under a Creative Commons Attribution-ShareAlike 4.0 License (International): http://creativecommons.org/licenses/by-sa/4.0

Version 1.0 | March 2020 www.MakersMakingChange.com

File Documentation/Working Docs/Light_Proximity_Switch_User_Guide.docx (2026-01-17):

Proximity Switch: Quick Guide

# Introduction

The proximity switch is an access switch that senses the motion of a hand, finger, or foot waved over a light sensor. This switch is suitable for users with some finger or hand movement, but limited strength, or for triggering assistive technology at a distance.

The unit works by detecting a shadow over its main sensor in an evenly lit environment. The sensitivity adjustments allow users and caretakers to change the sensing range up to 15cm.

# Features

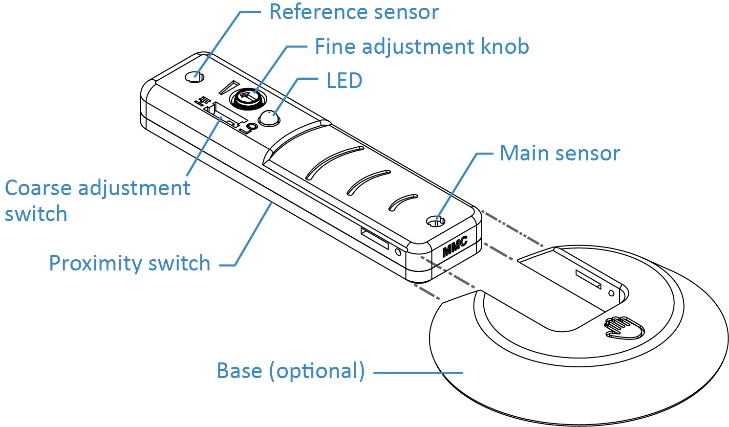
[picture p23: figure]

# Usage

1. Connect the 3.5mm audio cable from the proximity switch to the assistive device, and turn the fine adjustment knob fully clockwise. If the LED stays lit, dial the knob back (counter clockwise) until the LED goes out.
2. Wave your hand or finger over the main sensor. The LED will turn green when activated.

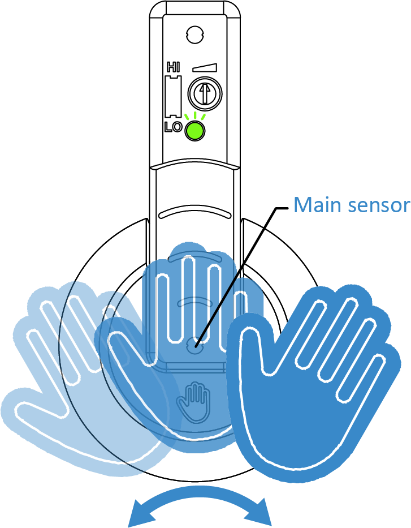
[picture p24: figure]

3. Adjust the sensitivity of the sensor using the adjustment knobs. 1. Coarse adjustment switch: Slide the switch using a pen to HI to detect up to 15cm of motion range and LO for up to 7.5cm

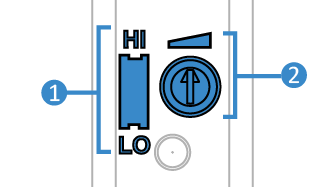
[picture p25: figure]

2. Fine adjustment knob:
Turn the fine adjustment knob with pen or fingernail towards the right to increase the sensitivity and towards the left to decrease it.

4. (Optional) For users low finger strength, slide and clip the 3D printed base to the proximity switch to use it as a ramp to reach the main sensor.

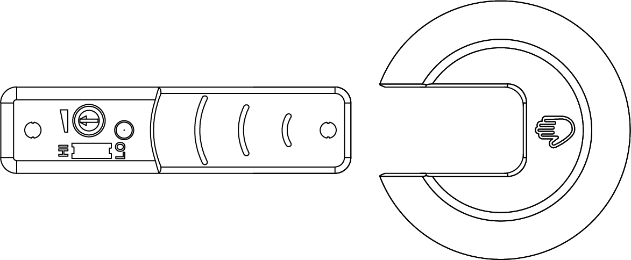
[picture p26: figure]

# Mounting Options

Adhere a strip of Velcro to the underside of the proximity switch for mounting.

# Changing the Battery

1. Flip the proximity switch over and use a Phillips screwdriver (+) to take out the two screws.

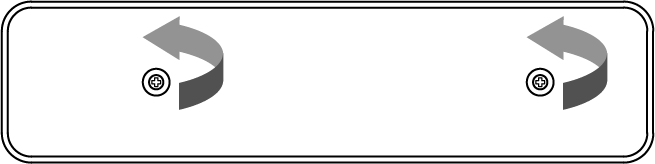
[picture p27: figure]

2. Take off the top case to reveal the battery.

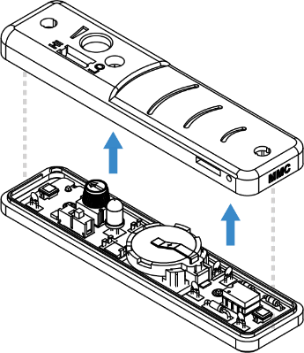
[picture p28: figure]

3. Take out the old battery using a small flathead screwdriver. Carefully pry out the battery from the highlighted area.

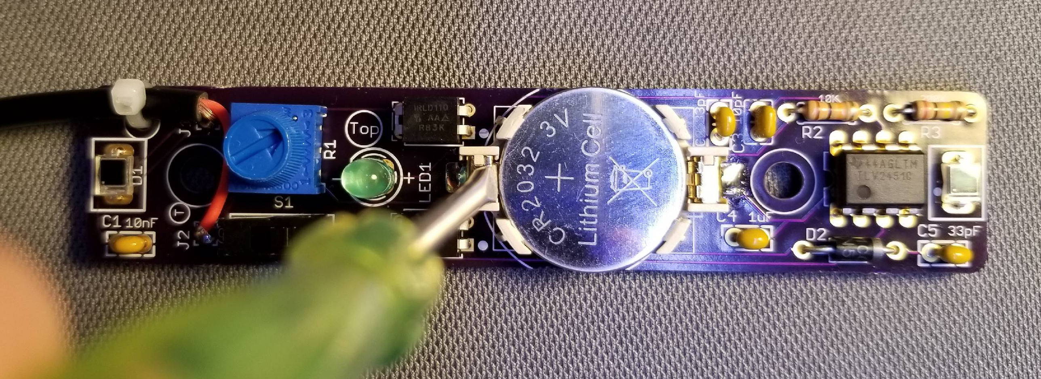
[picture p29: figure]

4. Replace with a new CR2032 coin cell battery.
5. Flip the proximity switch over and use a Phillips screwdriver (+) to take out the two screws.

# Lighting

For normal use, we recommend using the proximity switch under normal office lighting levels (150-500 lux), with the light source directly overhead for maximum sensing range. The proximity switch is capable working under a wide range of lighting levels, from approximately 4 lux (at a reduced range) to 107527 lux (full sunlight). Regardless of light level,

maximum range is achieved when the main light source is even, and directly facing the sensors on the proximity switch.

If the proximity switch is in the normal orientation (facing up) the light should be overhead. For side operation, the light source should face from the side, though for short range finger activation, the lighting requirements are less critical. Keep in mind, the proximity switch can be triggered by anything passing over the main sensor. Avoid placing the proximity switch anywhere where pets, birds, or equipment can walk, fly or swing over the main sensor.

# Cleaning

The 3D printed case of proximity switch can be wiped clean with a paper towel or soft cloth, using a mild household detergent solution. Non-toxic biodegradable all-purpose cleaners are preferred. If dust or particles fall into the light sensor wells, they can be gently swabbed out using a dry Q-Tip. Do not use abrasive cleaners, as they will scratch the surface of the unit. Do not submerge the unit in any liquid, as it will damage the internal electronic components. If disinfection is required, Isopropyl alcohol may be applied with a wipe.

# Specification

Specification | Details
Size | 110x27x14mm (switch only) 143x82x14mm (switch & base)
Battery | CR2032 cell, 3 volts (replaceable)
Battery Life | 6 months
Cord | 3mm switch plug cord length: 122cm (4 feet).

Neil Squire, 2020 © 2020 by Neil Squire. Proximity Switch Quick Guide is made available under a Creative Commons Attribution-ShareAlike 4.0 License (International): http://creativecommons.org/licenses/by-sa/4.0

Version 1.0 | March 2020 www.MakersMakingChange.com

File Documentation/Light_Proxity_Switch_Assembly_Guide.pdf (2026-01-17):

# Proximity Switch

# ASSEMBLY MANUAL

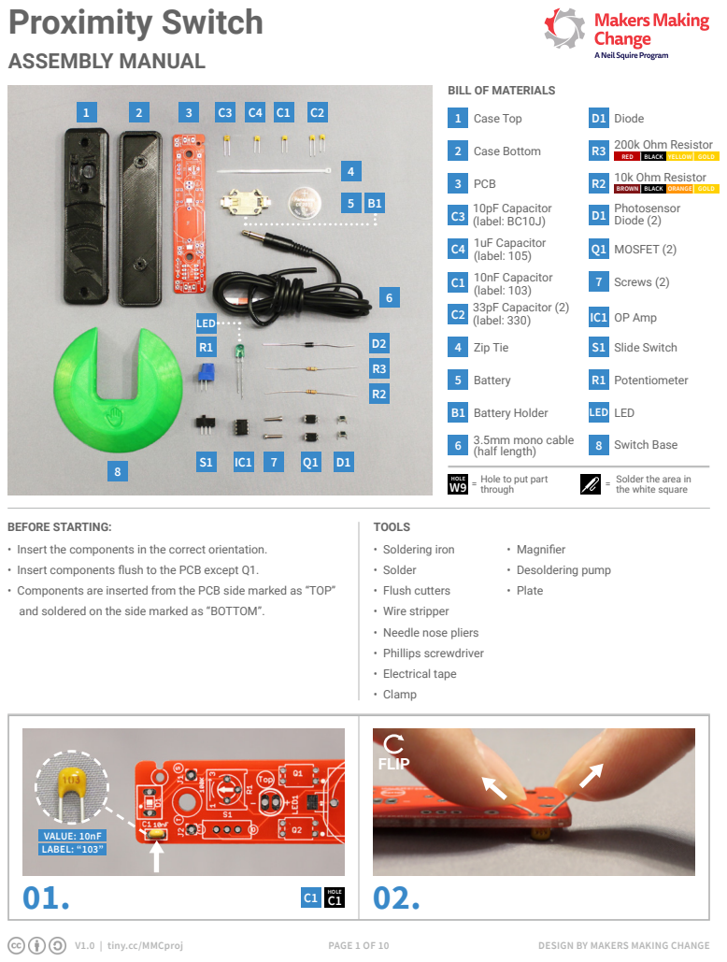
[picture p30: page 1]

BEFORE STARTING:
• Insert the components in the correct orientation.
• Insert components flush to the PCB except Q1.
• Components are inserted from the PCB side marked as “TOP”
and soldered on the side marked as “BOTTOM”.

# Proximity Switch

# ASSEMBLY MANUAL

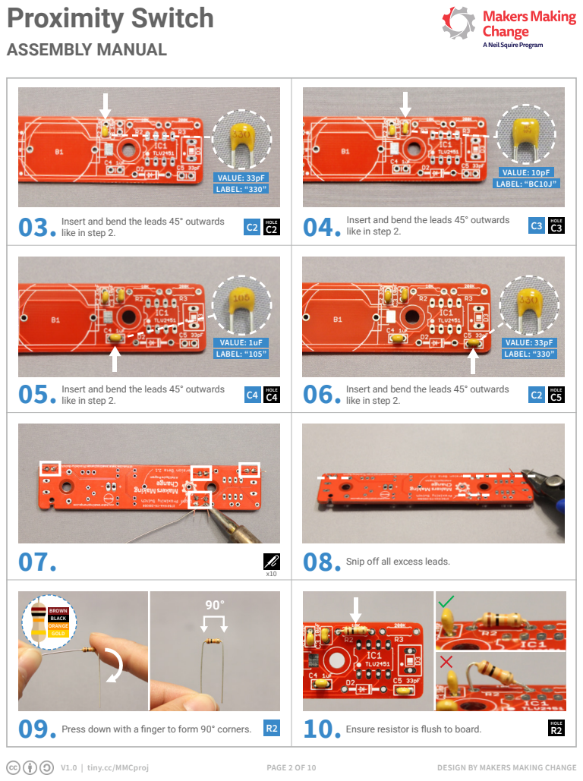
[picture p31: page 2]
V1.0 | tiny.cc/MMCproj; PAGE 2 OF 10; DESIGN BY MAKERS MAKING CHANGE; BROWN BLACK ORANGE GOLD; like in step 2.; HOLE C2; VALUE: 33pF LABEL: “330”; VALUE: 10pF LABEL: “BC10J”; HOLE C4; VALUE: 1uF LABEL: “105”

Insert and bend the leads 45° outwards

HOLE C3 Insert and bend the leads 45° outwards
like in step 2.

HOLE C2 Insert and bend the leads 45° outwards

Snip off all excess leads.

Press down with a finger to form 90° corners.

HOLE Ensure resistor is flush to board.

# Proximity Switch

# ASSEMBLY MANUAL

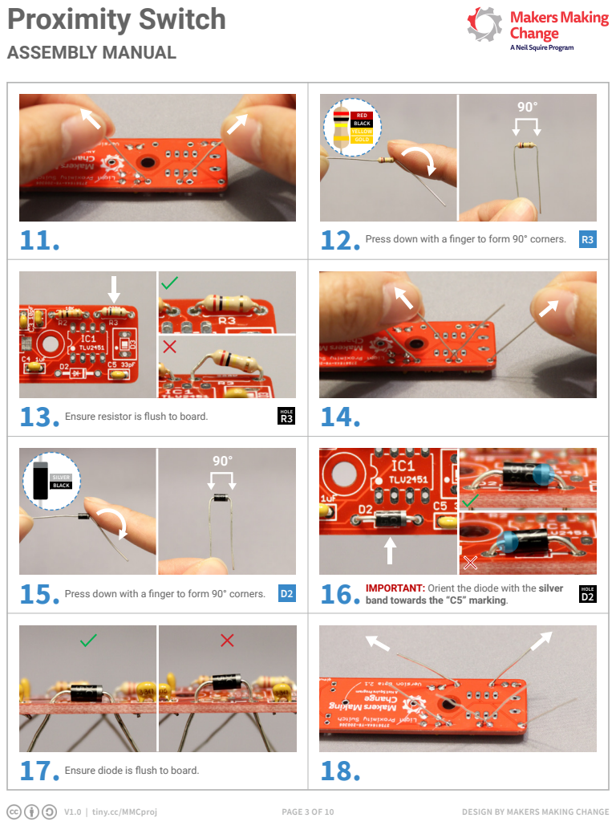
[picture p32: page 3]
V1.0 | tiny.cc/MMCproj; DESIGN BY MAKERS MAKING CHANGE; band towards the “C5” marking.; HOLE; PAGE 3 OF 10; RED BLACK YELLOW GOLD; SILVER BLACK

Press down with a finger to form 90° corners.

Ensure resistor is flush to board.

IMPORTANT: Orient the diode with the silver

Ensure diode is flush to board.

# Proximity Switch

# ASSEMBLY MANUAL

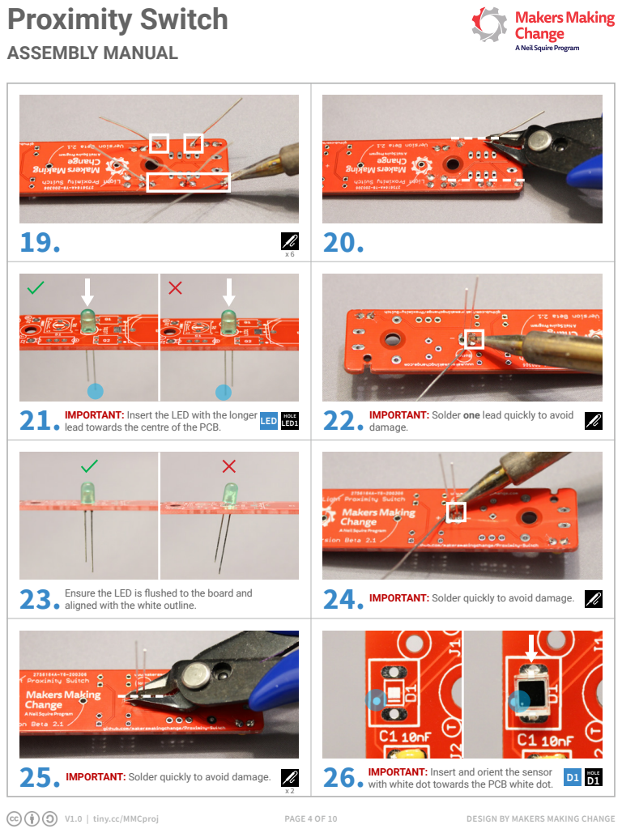
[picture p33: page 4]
V1.0 | tiny.cc/MMCproj; PAGE 4 OF 10; DESIGN BY MAKERS MAKING CHANGE; lead towards the centre of the PCB.; LED1; HOLE LED; with white dot towards the PCB white dot.; HOLE IMPORTANT: Solder quickly to avoid damage.

IMPORTANT: Insert the LED with the longer

IMPORTANT: Solder one lead quickly to avoid
damage.

Ensure the LED is flushed to the board and
aligned with the white outline.

IMPORTANT: Solder quickly to avoid damage.

IMPORTANT: Insert and orient the sensor

# Proximity Switch

# ASSEMBLY MANUAL

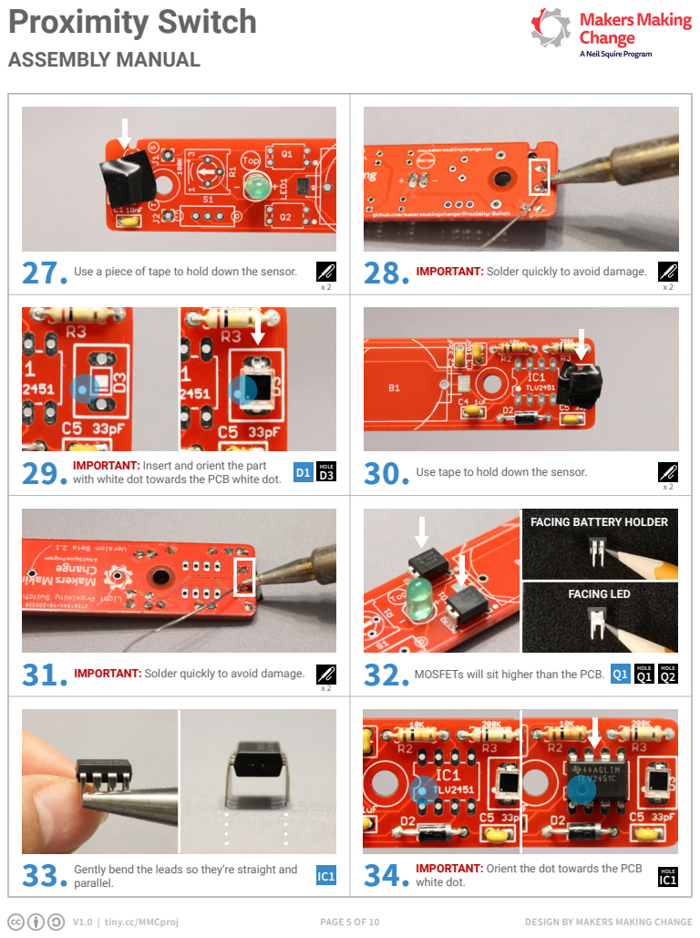
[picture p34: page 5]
V1.0 | tiny.cc/MMCproj; PAGE 5 OF 10; DESIGN BY MAKERS MAKING CHANGE; parallel. 33.; FACING LED; HOLE; HOLE IMPORTANT: Solder quickly to avoid damage.; MOSFETs will sit higher than the PCB. Q1; white dot.; with white dot towards the PCB white dot.; HOLE D1; Use tape to hold down the sensor.

Use a piece of tape to hold down the sensor.

IMPORTANT: Solder quickly to avoid damage.

IMPORTANT: Insert and orient the part

FACING BATTERY HOLDER

Gently bend the leads so they’re straight and

IMPORTANT: Orient the dot towards the PCB

# Proximity Switch

# ASSEMBLY MANUAL

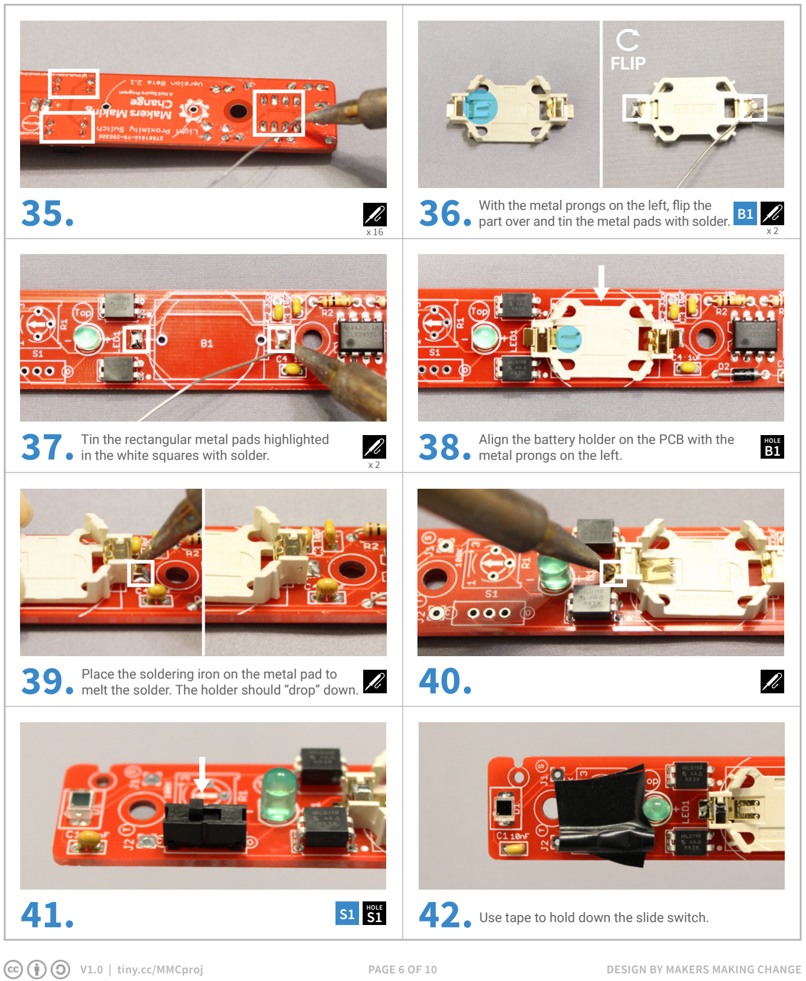
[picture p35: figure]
V1.0 | tiny.cc/MMCproj; PAGE 6 OF 10; DESIGN BY MAKERS MAKING CHANGE; FLIP; in the white squares with solder.; metal prongs on the left.; HOLE

35. 36. With the metal prongs on the left, flip the part over and tin the metal pads with solder.

Tin the rectangular metal pads highlighted

Place the soldering iron on the metal pad to 39. melt the solder. The holder should “drop” down.

Align the battery holder on the PCB with the

HOLE S1 | Use tape to hold down the slide switch.

# Proximity Switch

# ASSEMBLY MANUAL

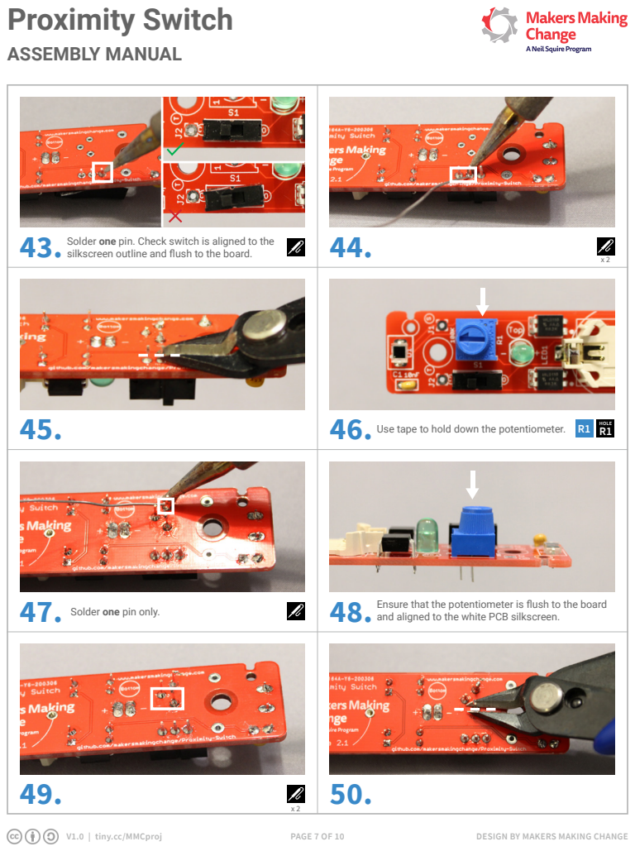
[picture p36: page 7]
PAGE 7 OF 10; HOLE Use tape to hold down the potentiometer.; Solder one pin only.; Ensure that the potentiometer is flush to the board

Solder one pin. Check switch is aligned to the
silkscreen outline and flush to the board.

47. 48. | and aligned to the white PCB silkscreen.

# Proximity Switch

# ASSEMBLY MANUAL

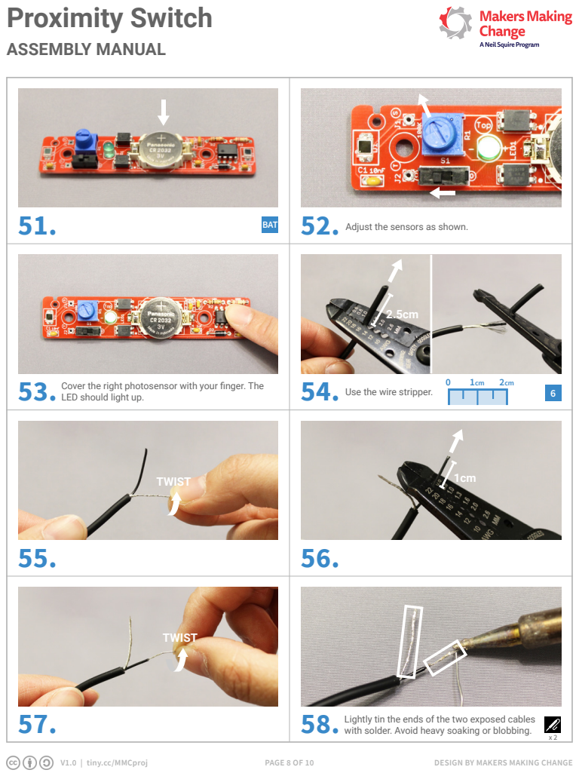
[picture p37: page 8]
PAGE 8 OF 10; with solder. Avoid heavy soaking or blobbing.; BAT; Adjust the sensors as shown.

Cover the right photosensor with your finger. The
LED should light up.

Use the wire stripper.

TWIST 55. 56. | 1cm

TWIST

Lightly tin the ends of the two exposed cables

# Proximity Switch

# ASSEMBLY MANUAL

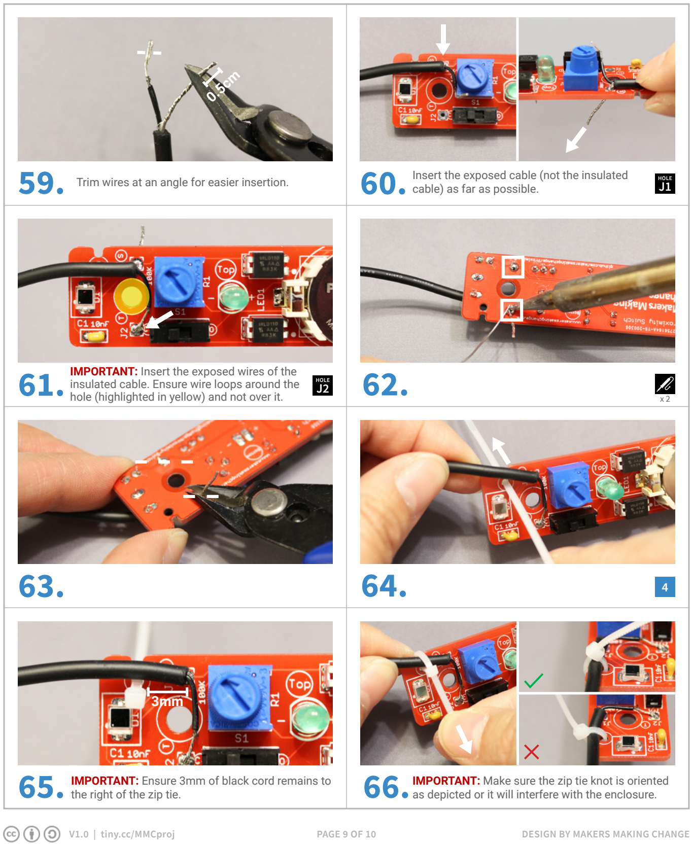
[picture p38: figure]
PAGE 9 OF 10; cable) as far as possible.; HOLE; the right of the zip tie.

### 59. Insert the exposed cable (not the insulated

insulated cable. Ensure wire loops around the hole (highlighted in yellow) and not over it. J2

IMPORTANT: Ensure 3mm of black cord remains to

IMPORTANT: Make sure the zip tie knot is oriented as depicted or it will interfere with the enclosure.

Trim wires at an angle for easier insertion.

IMPORTANT: Insert the exposed wires of the

# Proximity Switch

# ASSEMBLY MANUAL

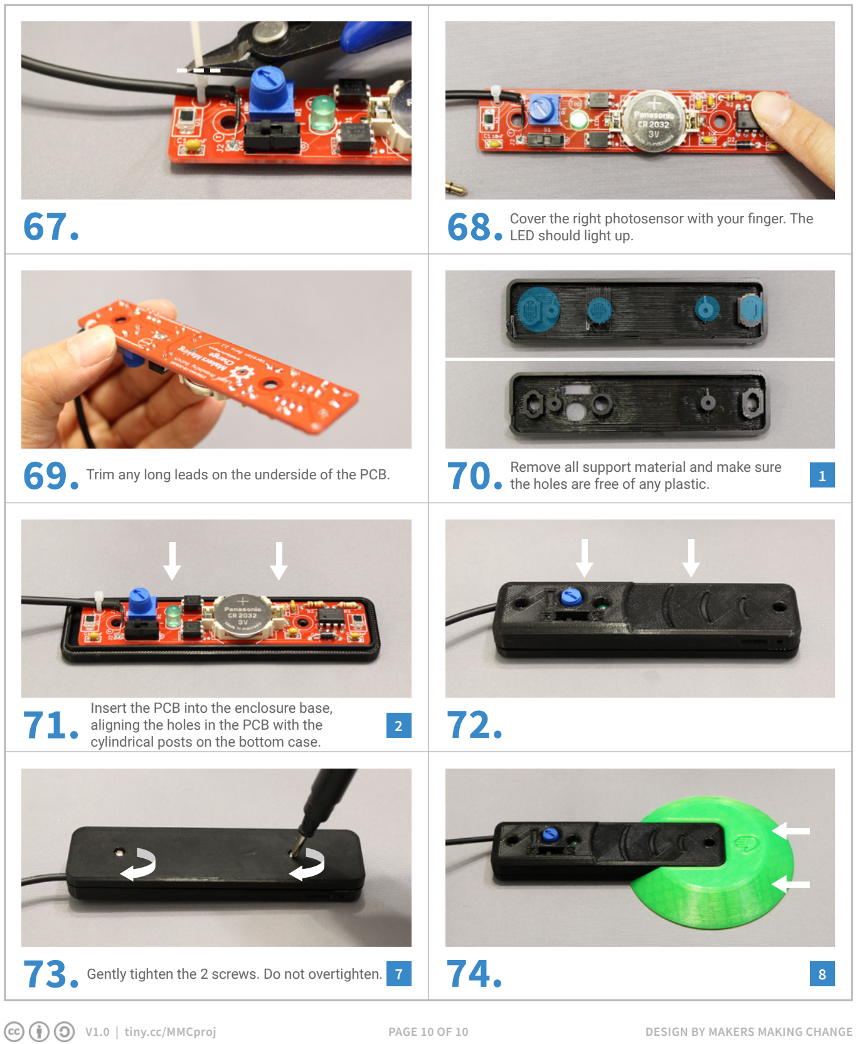
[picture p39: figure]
LED should light up.; the holes are free of any plastic.; Insert the PCB into the enclosure base, aligning the holes in the PCB with the cylindrical posts on the bottom case.; PAGE 10 OF 10

Cover the right photosensor with your finger. The

Trim any long leads on the underside of the PCB. | Remove all support material and make sure
Gently tighten the 2 screws. Do not overtighten. | 7 | 74. | 8

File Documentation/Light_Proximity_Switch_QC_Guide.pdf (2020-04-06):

## Proximity Switch: QC Guide

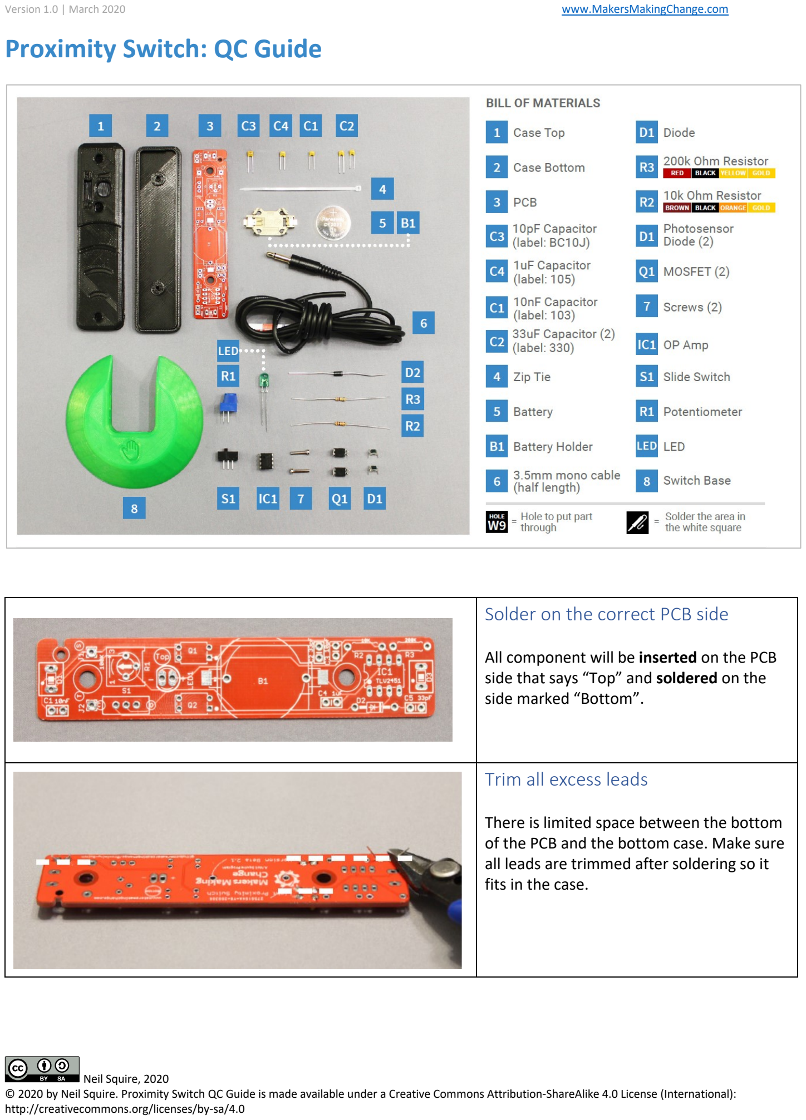
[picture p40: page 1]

Version 1.0 | March 2020 | www.MakersMakingChange.com

Neil Squire, 2020
© 2020 by Neil Squire. Proximity Switch QC Guide is made available under a Creative Commons Attribution-ShareAlike 4.0 License (International): http://creativecommons.org/licenses/by-sa/4.0

Solder on the correct PCB side All component will be inserted on the PCB side that says “Top” and soldered on the side marked “Bottom”.

Trim all excess leads There is limited space between the bottom of the PCB and the bottom case. Make sure all leads are trimmed after soldering so it fits in the case.

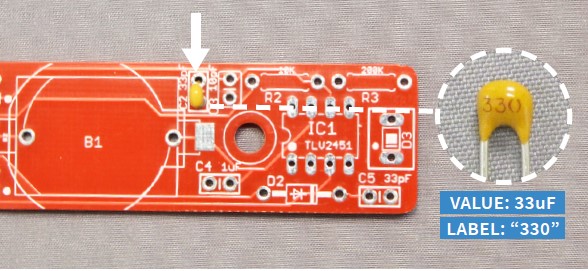
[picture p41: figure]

Capacitors Capacitors may look similar so look at the printed labelling to differentiate them.

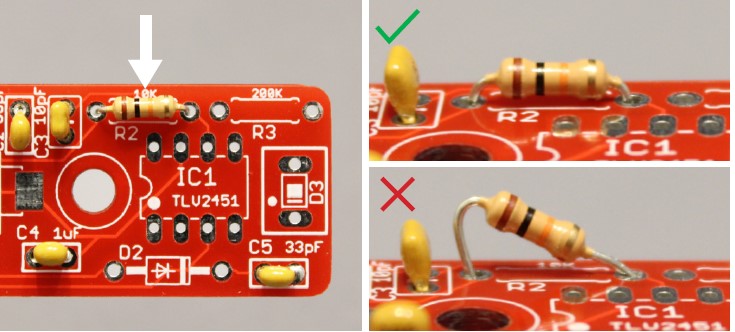
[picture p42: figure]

Ensure components are inserted flush to the board Components not soldered flush to the board may interfere with the case. A good tip is to solder one lead first, check to see if part is flush, and continue soldering.

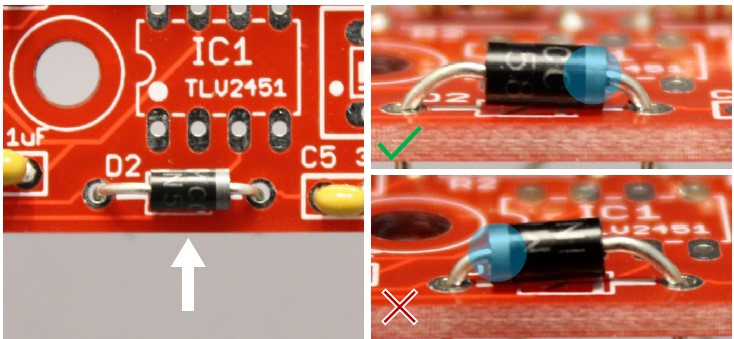
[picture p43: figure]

Diode Insert the diode with the silver band towards the C5 marking.

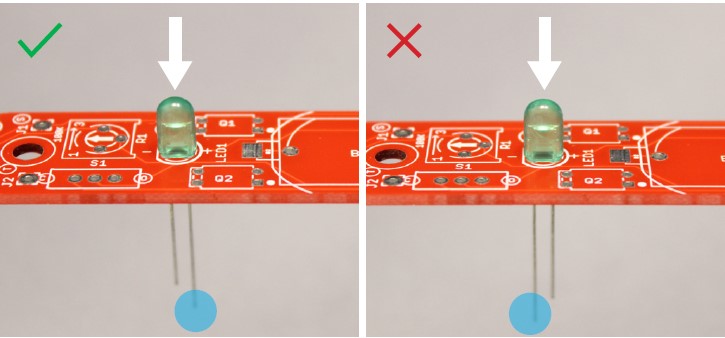
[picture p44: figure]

LED Insert the LED with the longer lead towards the centre of the PCB.

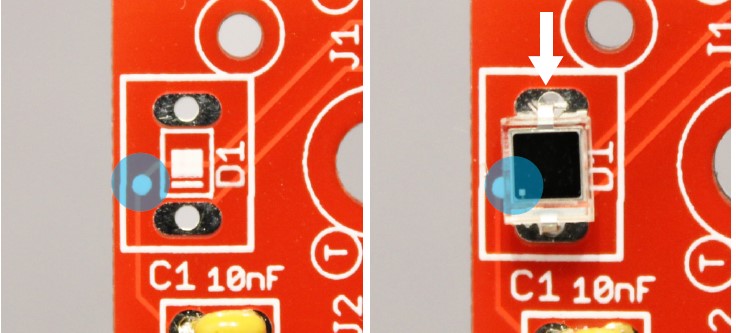
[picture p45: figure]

White dot Several components have white dots on the top. Align the white dot on the component with the white dot on the PCB.

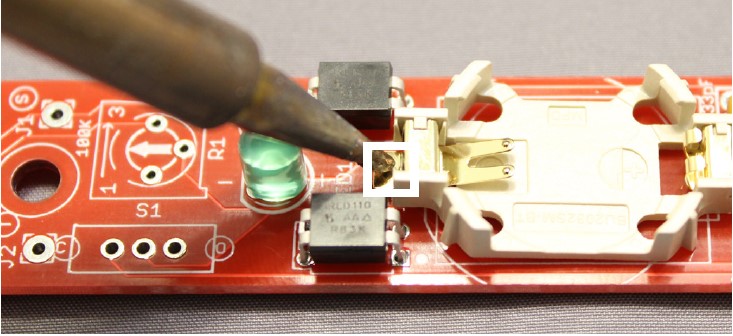
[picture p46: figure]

Soldering the battery holder Be careful of the soldering iron when soldering the battery holder to the PCB as the heat may damage surrounding components.

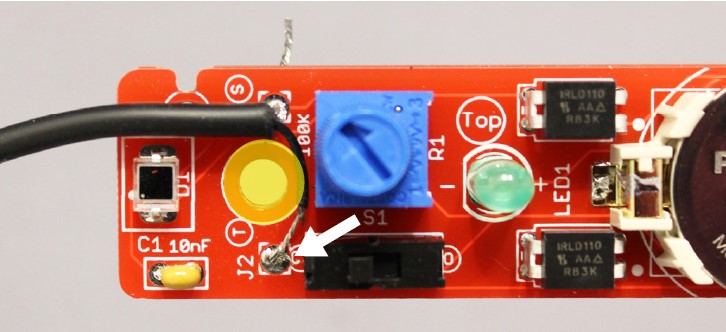
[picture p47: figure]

Mono cable When inserting and soldering the mono cable to the PCB, ensure enough clearance around the highlighted yellow circle.


Zip tie Cinch the zip tie in the depicted manner or else the knot will interfere with the case.


### Support Material

Remove all the support material from the top case.

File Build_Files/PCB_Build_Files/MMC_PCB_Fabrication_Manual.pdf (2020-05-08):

# MMC PCB Fabrication Manual

Version 1.0
2020/05/05

Makers Making Change
PCB Fabrication Manual | PCB Fabrication Manual
Version 1.0 | Page 2 of 10

## Table of Contents

## 1. Introduction

## 1.1. What is PCB?

PCB (Printed circuit board) is a board that has lines and pads that connect various points together. The board includes traces that electrically connect the various connectors and components to each other. A PCB allows signals and power to be routed between physical devices. Solder is the metal that makes the electrical connections between the surface of the PCB and the electronic components. [1]

## 1.2. What is PCB Fabrication?

PCB fabrication is the assembly method for circuit boards used in electronic devices. The layers of the board are put together along with the specific surface pattern based on the design files that is used in electronics manufacturing.[2]

## 1.3. What is gerber file?

Users create their own files for manufacturing based on the design files and send them to the manufacturer. The design files for manufacturing PCB is converted to a standard format known as a Gerber file. This is an industry standard for recording the specification of a PCB.[2]

## 2. PCB design tools

There are many different tools for designing PCB’s and you can select any of the available tools based on your previous experience or the requirements of your design. The process of designing PCB is not in the scope of this document but you can find courses or books that can help you understand the process of designing electronics circuits and PCB’s.

Here are the most common PCB design tools:

- Altium Designer (https://www.altium.com/) : Paid with Free Trial and student license.
- Eagle (https://www.autodesk.ca/en/products/eagle/) : Free limited version includes 2 schematic sheets, 2 signal layers, and an 80cm2 (12.4in2) board area.
- Kicad (https://www.kicad-pcb.org/) : Opensource with GNU’s GPL copyright agreement.
- Fritzing (https://fritzing.org/) : Opensource version available on github and the paid application is available. Limited options suitable for basic designs.
- Upverter (https://upverter.com/) : Free cloud-based design tool. It requires sign up for usage.

There are other available tools that can be used to design PCBs.

## 3. How to generate PCB gerber files for fabrication?

Once the PCB board file is created using your favorite PCB design tool then you can generate gerber files which is used by PCB fabrication companies to fabricate your design. The CAM processing tool uses the gerber generator file to create gerber files. The gerber generator file is usually provided by PCB fabrication company of your choice or can be created based on gerber files format which can be found on the website of the PCB fabrication company.

Each PCB board file includes different top and bottom layers and gerber files provide specifications for each of these layers by combining layers together based on the format specified by gerber file generator.

Common layers:

- Top & Bottom Copper
- Top & Bottom Silkscreen
- Top & Bottom Soldermask
- Drill
- Drill Station Info
- Photoplotter Info
- Mill Layer
- Top Paste

There is no standard format for the gerber file generator and there are variations of formats used by PCB fabrication companies.

You can find the final generated gerber files of the projects involving PCB designs for common PCB fabrication companies on our website. You can use the generated gerber files available if you are using one of the fabrication companies listed below or you can create your own gerber files based on PCB design files.

- Seeed Fusion PCB (https://www.seeedstudio.com/fusion.html)
- PCBWay (https://www.pcbway.com/)
- OSH Park ~ (https://oshpark.com/)
- JLCPCB (https://jlcpcb.com/)

We now go over process of generating gerber files using three common PCB design tools.

## Eagle

1. Open the board file of your PCB design using Eagle
2. Select File > CAM Processor
3. Click on “Load job file” dropdown menu button and select “Open CAM file”
4. Download or create the gerber generator file (.cam) used by your PCB fabrication company of your choice
5. Navigate in your system and find the directory that includes the gerber file generator file with. cam extension
6. Select the gerber file generator file and click on “Open” button
7. Double check the Output file layers on left menu bar to make sure there are no layers are missing
8. Click on “Process Job” button
9. Select the output directory (Create a new directory called “gerbers” as an example)
10. The process of creating the gerber file will start and finish once you receive a popup message indicating that “Job Proceed Successfully!”
11. Click on “OK” button
12. Navigate to the directory that includes the generated gerber files (“gerbers” directory as an example)
13. Select all the gerber/drill files in the directory that saved them and generate a compressed file in Zip format.
14. You can now submit the compressed Zip file that includes the gerber files to the PCB fabrication company of your choice.

## Altium designer

1. Open the board file of your .PCB design file using Altium designer. [3]
2. Select File > Fabrication Outputs > Gerber Files
3. Select General setting in Gerber Setup window
4. Set the units in “inches” precision to “2:5” in General setting
5. Select Layers setting in Gerber Setup window
6. Next, make sure you have the clear outline in mechanical layer.

7. Check the layers in “Plot” column under “Layers To Plot” section for creating gerber files according to fabrication company instructions.
- Check following layers: GTO, GTP, GTS, GTL, GBL , GBS , GBP , GBO , GKO ,GPT , GPB , GM(Number)
- There will be no middle layer if you PCB board includes only 2-layers. All our design files include 2 layers which means you need to uncheck all middle layers (G1,G2,G3....)
- You can use the “Plot Layer” option and select the “Used On” to automatically check the used layers in your design.
8. Select “All Off” in “Mirror Layers” or uncheck every layer in “Mirror Layers” column
9. Uncheck all the layers in the plot column of “Mechanical Layers to Add to All Gerber Plots”
10. Check “Embedded apertures (RS274X)” under “Aperture” setting
11. Click on the “OK” button to generate gerber files.
12. Gerber files are automatically loaded in the Altium cam viewer. You can use “CAMtastic” view to verify that all layers have been generated correctly.
13. The gerber files should now be generated and saved in directory of your project.
14. You can also export gerber files to a new directory using following steps:
- Select File > Export > Gerber…
- Click on “OK”
- Select the path to the directory that you would like to save all the gerber files. (“gerbers” directory as example)
- Click on “OK” to export all the gerber files
15. Next, Generate the Drilling layer in Excellon format
16. Select File > Fabrication Outputs > NC Drill Files
17. Set the units in “inches” precision to “2:5” in NC Drill Setup window
18. Click on the “OK” button to generate drill files
19. The drill file should now be generated and saved as .TXT file in directory of your project.
20. You can also export file to a new directory using following steps:
- Select File > Export > Save Drill…
- Click on “OK”
- Select the path to the directory that you would like to save the drill file. (“gerbers” directory as example)
- Click on “OK” to export the drill file
21. Select the “Projects” view and highlight the “CAMtastic” cam file
22. Click on “Save As” under “File” and save the “CAMtastic” cam file.
23. Click on “Save”.
24. Select all the gerber/drill files in the directory that saved them and generate a compressed file in Zip format.

25. You can now submit the compressed Zip file that includes the gerber files to the PCB fabrication company of your choice.

## Kicad

1. Open the board file of your design file using Kicad. [4]
2. Select File > Plot
3. Check the layers in “Plot” window for creating gerber files according to fabrication company instructions.
- Check following layers: Top Copper (F.Cu), Soldermask (F.Mask), Silkscreen (F.SilkS), Bottom Copper (B.Cu), Soldermask (B.Mask), Silkscreen (B.SilkS), Board outline (Edge.Cuts)
4. Set the “Output directory” to save the generated gerber files. You can also use “Browse…” button to set the path to the directory.
5. Uncheck “Plot sheet reference on all layers” option.
6. Uncheck “Plot footprint values” option.
7. Check “Exclude PCB edge layer from other layers” option.
8. Check “Use Protel filename extensions” option.
9. Click on “Plot” button to generate and save gerber files in the specified output directory to save gerber files.
10. Next, configure the settings to generate drill file
11. Click on “Generate Drill File” button.
12. Set the “Output directory” to save the generated drill file. You can also use “Browse…” button to set the path to the directory. Use the same output directory as you selected to save the gerber files.
13. Check “Inches” as drill units.
14. Check “Decimal Format” as zeros format.
15. Check “PostScript” as drill map file format.
16. Check the “Merge PTH and NPTH holes into one file” option
17. Click on “Drill File” or press “Enter” to generate the drill file.
18. Click on “Close” to close “Drill Files Generation” Window.
19. Click on “Close” again to close “Plot” Window.
20. Verify the generated gerber files using a gerber viewer tool to make sure that all layers have been generated correctly.
21. Select all the gerber/drill files in the directory that saved them and generate a compressed file in Zip format.
22. You can now submit the compressed Zip file that includes the gerber files to the PCB fabrication company of your choice.

## 4. How to check and confirm PCB gerber files?

It is recommended to double check or triple check the final generated gerber files of your design to make sure there are no issues with process of gerber files generation. The PCB fabrication companies mostly provide online gerber file viewer tools that you can use to confirm your design once you upload your gerber files compressed as a Zip file. However, you can use other gerber file viewer to check your design files before submitting the gerber files.

The following gerber viewer tools are recommended:

- Online Gerber Viewer (https://www.gerber-viewer.com/)
- gerbv (https://sourceforge.net/projects/gerbv/)

Select all the generated gerber file layers in the “gerbers” directory and view them to make sure all the layers are aligned.

## 5. Where to send PCB gerber files for fabrication?

The process to send the gerber files for fabrication may differ from company to company but there are general steps you can follow to send your gerber files for fabrication.

1. Select the fabrication company (Here are our recommended fabrication companies)
- Seeed Fusion PCB
- PCBWay
- OSH Park ~
- JLCPCB
2. Create an account on PCB fabrication website or use temporary login if it is available
3. Select the fabrication service
4. Upload the compressed Zip file that includes your gerber files
5. Select the available options based on your design requirements. The standard options for most of our projects:
- PCB Layers: 2 Layers
- PCB dimensions should update based on your uploaded gerber files, but you can manually entry the dimensions as well
- PCB quantity can vary based on your requirements (Minimum 5)
- PCB Color can be changed if the fabrication company offers the option. The defualt option has the fastest turnaround time.
- Surface Finish: HASL
- Copper Weight, Minimum Drill Hole Size, Trace Width , Minimum Solder Mask Dam doesn’t require to be changed and the default value works
6. Check the uploaded gerber files using online gerber viewer tool if it is offered by the fabrication company and make sure there are no issues.

7. Add the uploaded design to the order
8. Add another design if you are doing multiple orders
9. Proceed to the checkout and enter your billing and shipment information
10. Select the shipping method
11. Submit your order for production
12. The technician will contact you for additional information or corrected files if there are issues with your design files.
13. You will receive an email when your design goes to production
14. You will receive another email once your PCBs are produced and shipped

This includes the instructions for fabrication of PCB designs based on generated gerber files.

## Reference

1. https://learn.sparkfun.com/tutorials/pcb-basics/all
2. https://www.hi5electronics.co.uk/what-is-pcb-fabrication/
3. https://support.jlcpcb.com/article/42-how-to-export-altium-pcb-to-gerber-files
4. https://support.jlcpcb.com/article/44-how-to-export-kicad-pcb-to-gerber-files

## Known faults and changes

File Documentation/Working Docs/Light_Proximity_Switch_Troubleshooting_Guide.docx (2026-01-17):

# Light Proximity Switch Troubleshooting Guide

The Light Proximity Touch Switch Troubleshooting Guide covers troubleshooting and repair of the Light Proximity Switch (https://www.makersmakingchange.com/project/light-proximity-switch/). The most common failures are likely to include parts placed in backwards, typically the photodiodes, and main IC.

### Tools needed for testing:

- Screwdriver
- Digital multimeter (do not use analog meters unless VTVM type)
- Small penlight type flashlight

### Tools needed for repair:

- Wire cutters
- Soldering iron
- Solder
- Soldering pump or solder wick braid
- Two alligator clip jumper wires
- Black electrical tape (must be coloured black)

### Checking for proper battery power

Set the multimeter to the 20 V Range. On the PCB, attach the negative lead to the gold colored battery tab closest to the LED. Attach the positive lead to the gold colored battery tab closest to the main IC chip . You should be able to measure a voltage of between 2.7V and 3.3V on your meter. If the battery is low, replace the battery.

### Main troubleshooting

Photo DIODES:

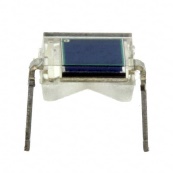
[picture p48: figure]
BPW34

Begin by checking the main sensor photodiodes (small black squares on left and right of PCB). Set the multimeter to the 5V Range. Attach the positive lead of the multimeter to the lower (dot side) pin of the left photodiode, and the negative lead to the upper pin of the photodiode. Shine the penlight on the sensor, and you should see the voltage rise to above 0.2 volts. Repeat with the right side photodiode. If you don’t see a voltage increase the photodiode should be replaced. If the voltage reading shows negative (minus sign) the photodiode is in backwards, and should be reinstalled properly.

IC CHIP:

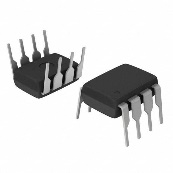
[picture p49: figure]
8-DIP

While shining the penlight on the left photodiode, and a small piece of electrical tape on the right photodiode, measure the voltage between pins 2 and 3 on the IC. make sure the negative lead of the multimeter is on pin 2. You should read a positive voltage in the 0.2 volt range. Now, place the negative lead of the multimeter on pin 4 of the IC, and the positive lead on pin 6. You should read a positive voltage between 2.5 and 3.2 volts. If the reading is correct, the LED should be lit. If the LED isn’t lit, it may be in backwards, or dead.

While shining the penlight on the right photodiode, and a small piece of electrical tape on the left photodiode, measure the voltage between pins 2 and 3 on the IC. make sure the negative lead of the multimeter is on pin 2. You should read a negative voltage in the 0.2 volt range. Now, place the negative lead of the multimeter on pin 4 of the IC, and the positive lead on pin 6. You should read a voltage close to 0 volts. If the reading is correct, the LED should be off.

PAGE 1 OF 3

Solid State relay (Mosfets):

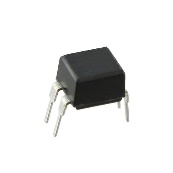
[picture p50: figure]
4-DIP

The Mosfets are the two black rectangles between the LED and the battery. While shining the penlight on the left photodiode, and a small piece of electrical tape on the right photodiode, confirm the LED is on. Measure the voltage across the two right side pins of each Mosfet (positive lead of the multimeter to pin marked with white dot) You should read a positive voltage between 2.5 and 3.2 volts, for each Mosfet.

Next, set your multimeter to CONTINUITY mode. Measure between each Mosfet drain pin (pin tab on left) and the source pin (pin without white dot on right) With the positive lead of the multimeter on the drain tab (on left side Mosfet). Make sure your meter beeps or shows less than 8 ohms. As part of each test, remove the tape and light, and turn the sensitivity fully counter-clockwise. The continuity reading should show “0” or off, (open circuit) when you do this.

Cable test

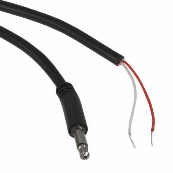
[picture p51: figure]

The final step, will be to confirm the cable isn’t open or shorted. With the Proximity switch off, (LED not lit), measure the continuity between solder joints J1 and J2 on the PCB (where the cord is soldered to the board) The continuity reading should show “0” or off. Now, measure continuity between the tip of the plug and solder joint J2. The reading should be “1” (or less than 4 ohms). Now, measure continuity between the metal sleeve of the plug (metal area behind tip) and solder joint J1. The reading should be “1” (or less than 4 ohms). If you get a zero reading testing J1 and J2, replace the cord.

Printed Circuit Board (main PCB):

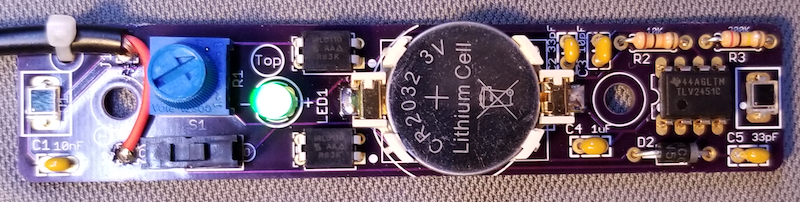
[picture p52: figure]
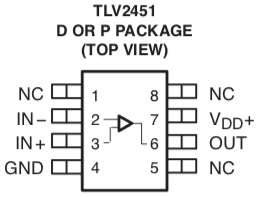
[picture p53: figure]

Schematic Diagram:

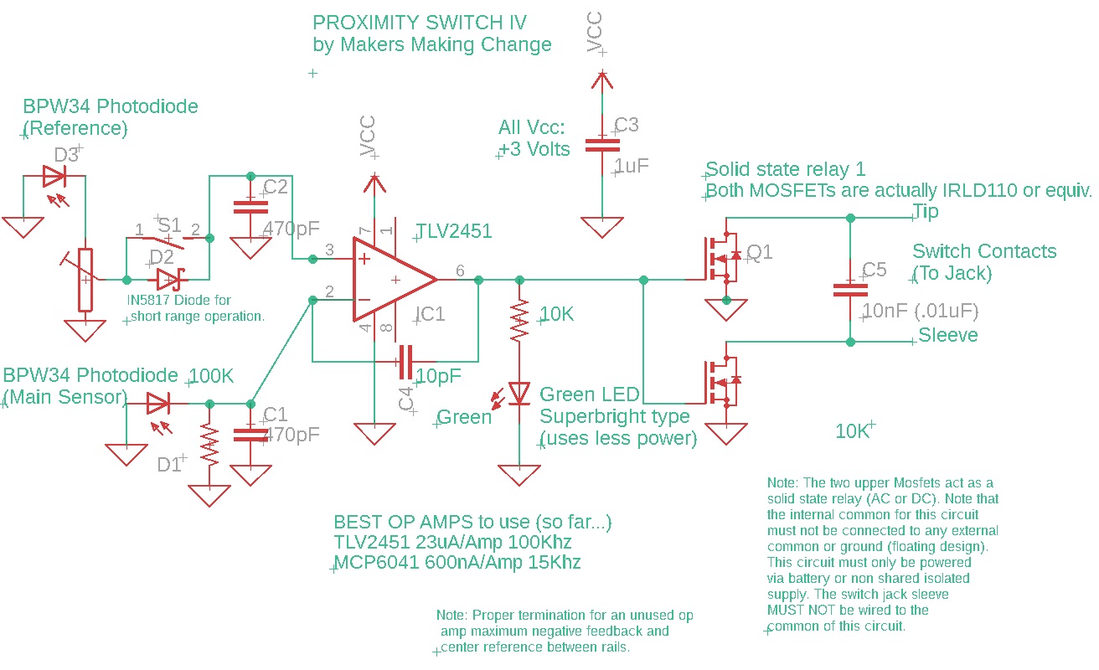
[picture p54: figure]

PAGE 2 OF 3

### Parts List:

1 OP amp TLV2451 296-1889-5-ND

2 Mosfet IRLD110 IRLD110PBF-ND

2 Photodiode BPW34 475-1070-ND

1 DIODE SCHOTTKY 20V 1A DO41 1N5817-TPCT-ND

1 Superbright LED Green 5mm standard profile C566C-GFF-CX0Y0892CT-ND

1 Capacitor 10pF 6v 445-180508-1-ND

2 Capacitor 470 pf *399-9740-ND

1 Capacitor 10nF 50v *399-4148-ND

1 Capacitor 1uF 6v *399-9714-ND

1 Resistor 10k 1/4 watt *S10KQCT-ND

1 CR2032 battery holder BU2032SM-FH-GCT-ND

PAGE 3 OF 3

www.MakersMakingChange.com

Version 1.0 | January 2021

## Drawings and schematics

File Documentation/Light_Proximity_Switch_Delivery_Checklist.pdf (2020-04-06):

# Maker To Do

## ☐ Build the Light Proximity Switch

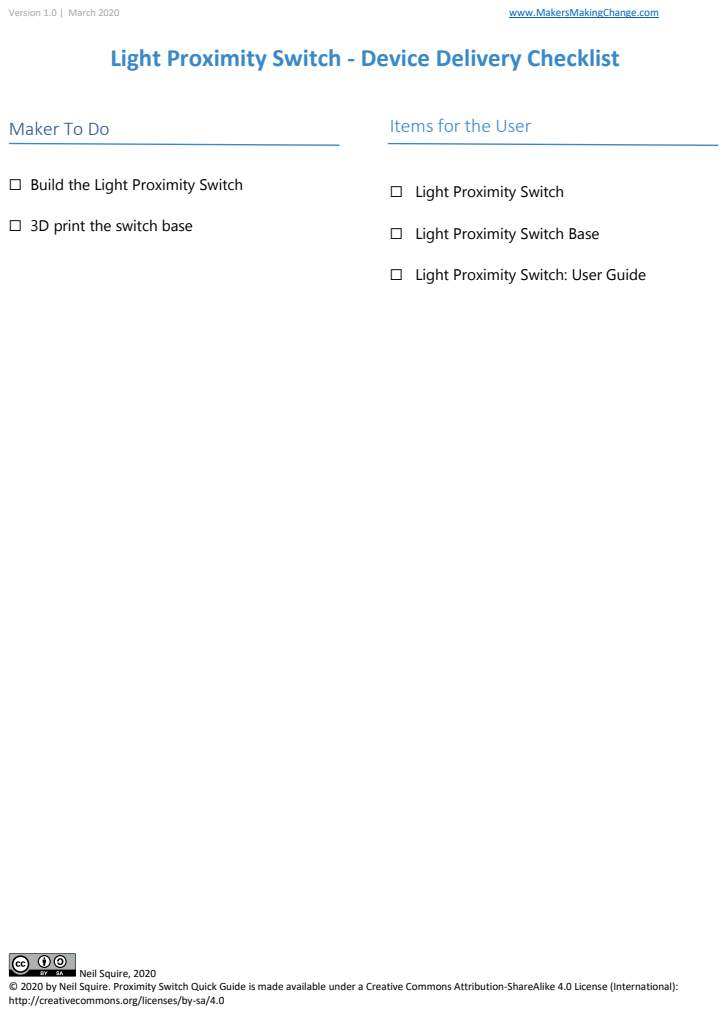
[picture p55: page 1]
Version 1.0 | March 2020; www.MakersMakingChange.com; Neil Squire, 2020

Light Proximity Switch - Device Delivery Checklist

Items for the User

☐ Light Proximity Switch

☐ 3D print the switch base

☐ Light Proximity Switch Base

☐ Light Proximity Switch: User Guide

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

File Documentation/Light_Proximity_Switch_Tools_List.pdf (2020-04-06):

# Proximity Switch: Tool List

# Tools

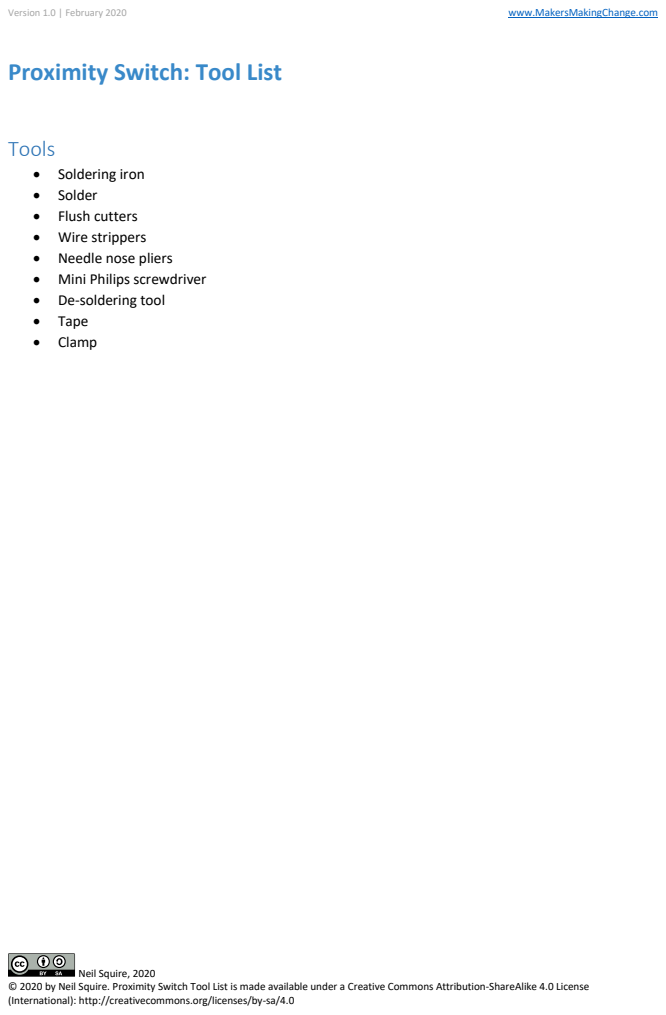
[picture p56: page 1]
Version 1.0 | February 2020; www.MakersMakingChange.com; Neil Squire, 2020

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

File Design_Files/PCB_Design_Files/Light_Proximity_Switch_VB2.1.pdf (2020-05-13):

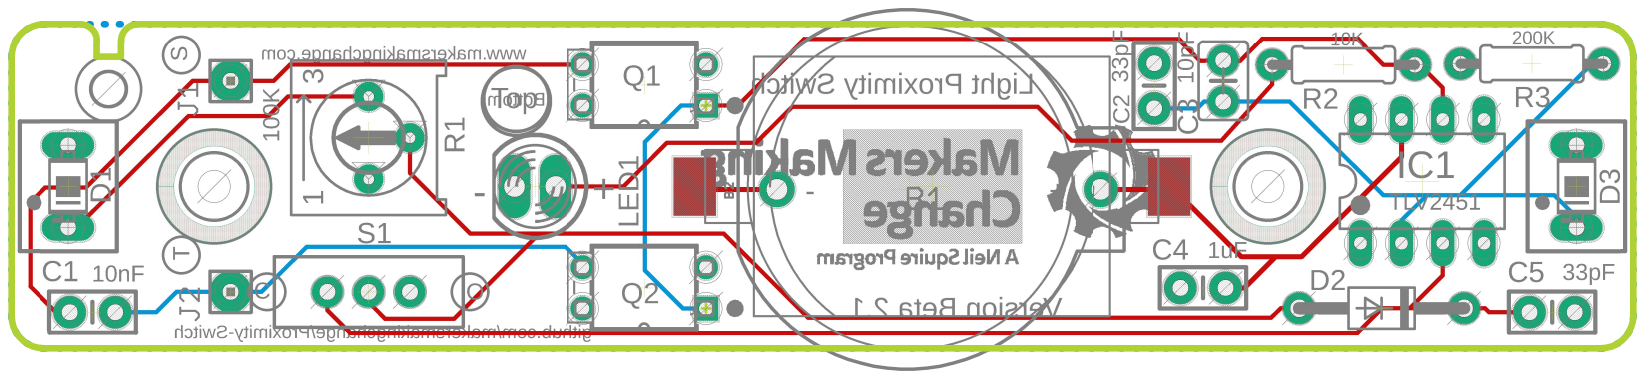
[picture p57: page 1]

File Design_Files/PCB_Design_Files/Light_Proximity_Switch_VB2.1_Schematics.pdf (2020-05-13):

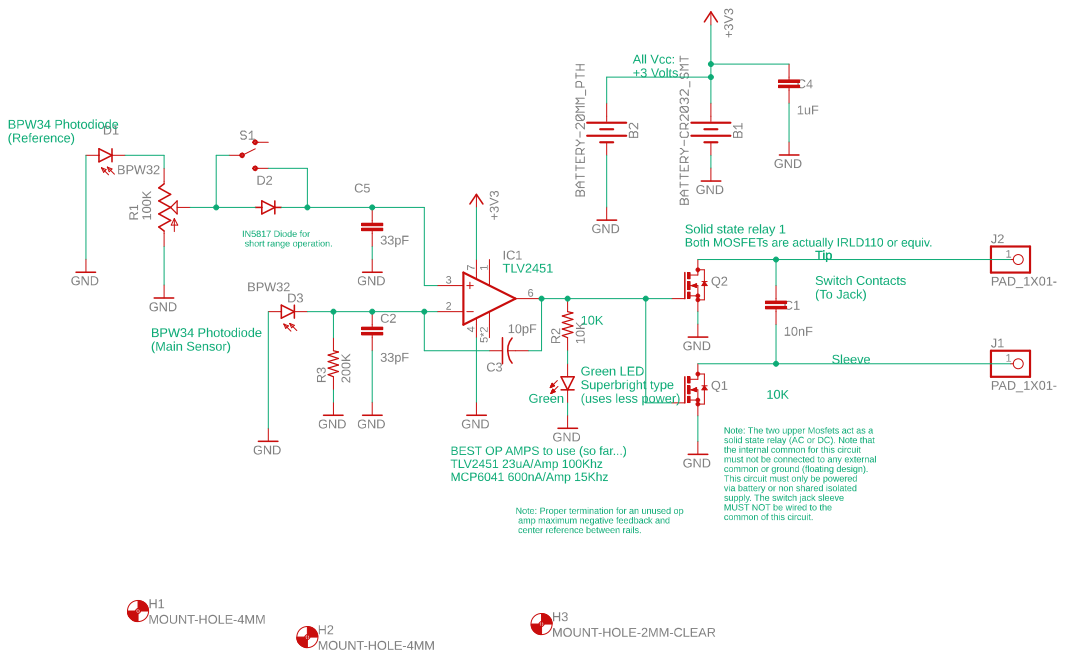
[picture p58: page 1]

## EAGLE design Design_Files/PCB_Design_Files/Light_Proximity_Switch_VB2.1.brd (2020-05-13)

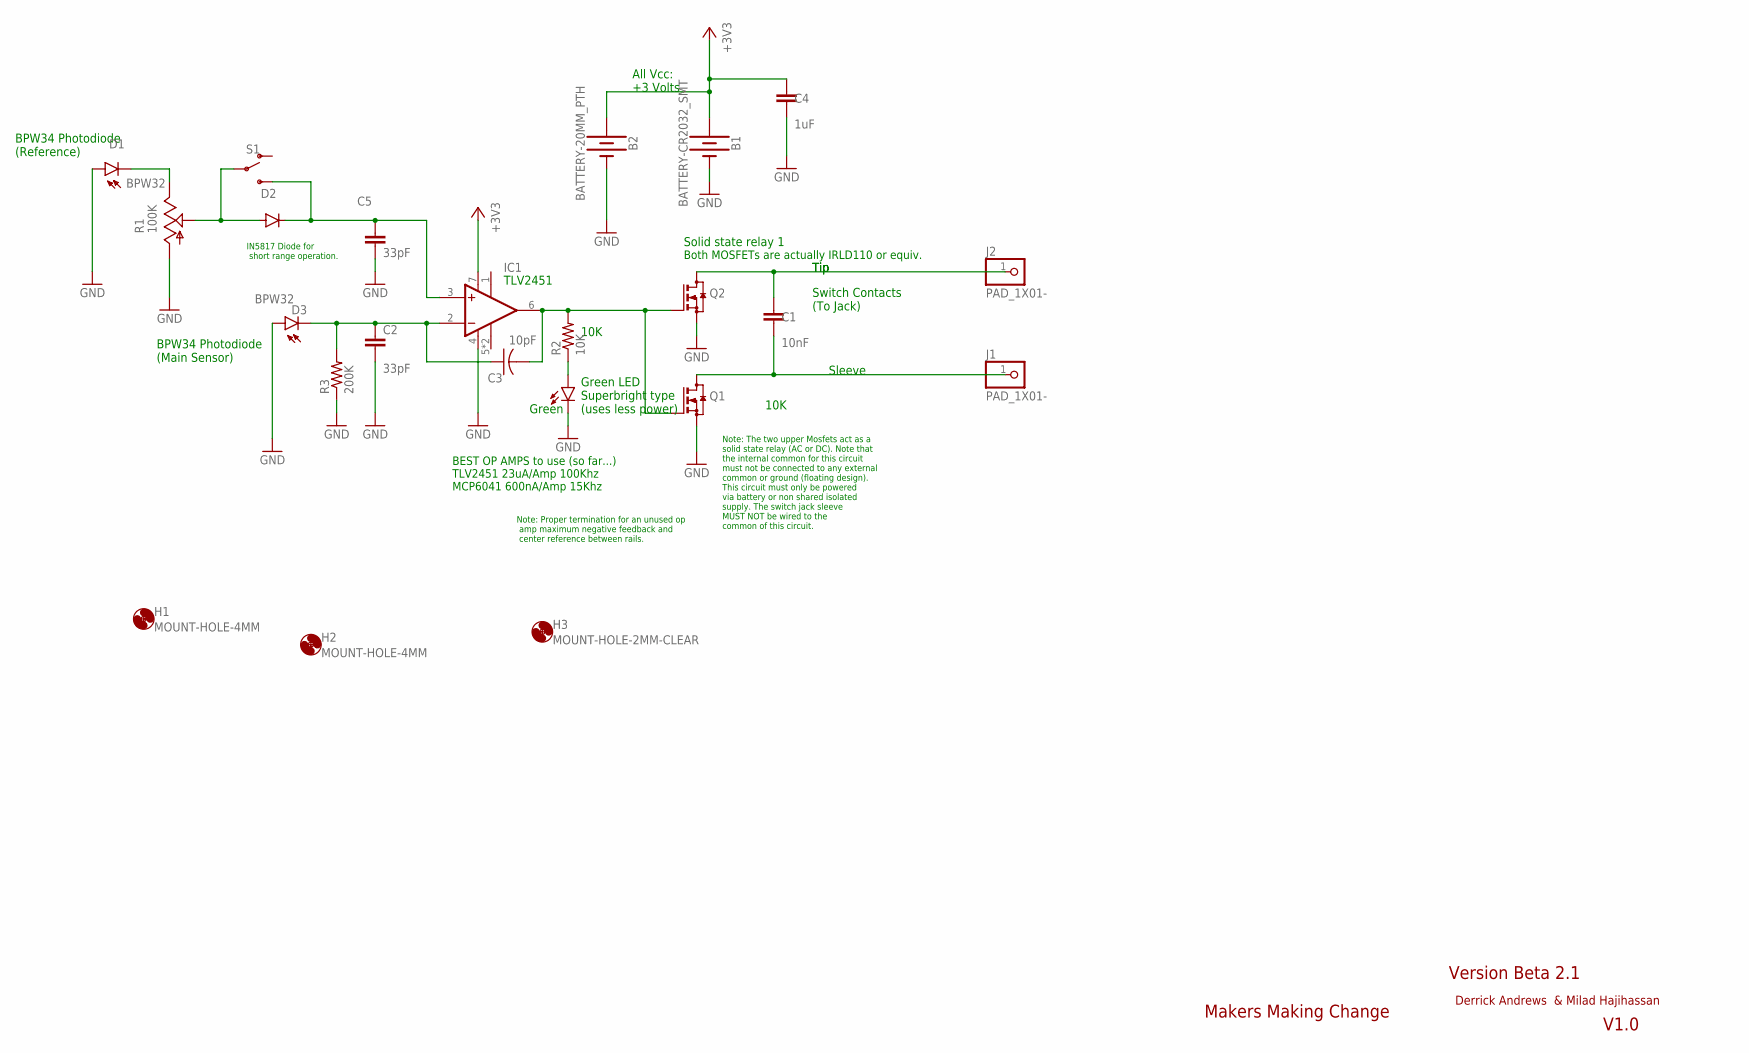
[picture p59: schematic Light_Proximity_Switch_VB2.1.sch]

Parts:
B1: BATTERY-CR2032_SMT; CR2032_SMT_HOLDER
B2: BATTERY-20MM_PTH; BATTCOM_20MM_PTH
C1: 10nF; CAP-PTH-SMALL-KIT
C2, C5: 33pF; CAP-PTH-SMALL-KIT
C3: 10pF; C025-030X050
C4: 1uF; CAP-PTH-SMALL-KIT
D1, D3: BPW32
D2: DIODE-DO41; DO41-10
H1, H2: MOUNT-HOLE-4MM; HOLE-4MM
H3: MOUNT-HOLE-2MM-CLEAR; HOLE-2MM-CLEAR
IC1: TLV2451; DIL08
J1, J2: PAD_1X01-; PAD-1X01
LED1: LED_5MM-5MM-GREEN; LED_5MM_GREEN
Q1, Q2: IRLD110-HVM-DIP; HVM-DIP
R1: 100K; 3386P-T
R2: 10K; RESISTOR_0206/8
R3: 200K; RESISTOR_0206/8
S1: SWITCH-SPDT-PTH_11.6X4.0MM; SWITCH_SPDT_PTH_11.6X4.0MM

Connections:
+3V3: B1.+, B2.+, C4.1, IC1.7 (V+)
GND: B1.-, B2.-, C2.2, C4.2, C5.2, D1.A, D3.A, IC1.4 (V-), LED1.K (C), Q1.2 (S), Q2.2 (S), R1.A, R3.1
unnamed: D2.A, R1.S, S1.2
unnamed: C5.1, D2.C, IC1.3 (+IN), S1.3 (S)
unnamed: D1.K (C), R1.E
unnamed: C3.2, IC1.6 (OUT), Q1.1 (G), Q2.1 (G), R2.2
unnamed: C1.2, J1.1, Q1.3 (D)
unnamed: C1.1, J2.1, Q2.3 (D)
unnamed: C2.1, C3.1, D3.K (C), IC1.2 (-IN), R3.2
unnamed: LED1.A, R2.1

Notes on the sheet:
Makers Making Change
V1.0
Derrick Andrews & Milad Hajihassan
All Vcc: +3 Volts
Switch Contacts (To Jack)
10K
Note: The two upper Mosfets act as a solid state relay (AC or DC). Note that the internal common for this circuit must not be connected to any external common or ground (floating design). This circuit must only be powered via battery or non shared isolated supply. The switch jack sleeve MUST NOT be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
Tip
Sleeve
Solid state relay 1
Green LED Superbright type (uses less power)
Green
BEST OP AMPS to use (so far...) TLV2451 23uA/Amp 100Khz MCP6041 600nA/Amp 15Khz
BPW34 Photodiode (Main Sensor)
BPW34 Photodiode (Reference)
Note: Proper termination for an unused op amp maximum negative feedback and center reference between rails.
Both MOSFETs are actually IRLD110 or equiv.
IN5817 Diode for short range operation.
TLV2451
Version Beta 2.1

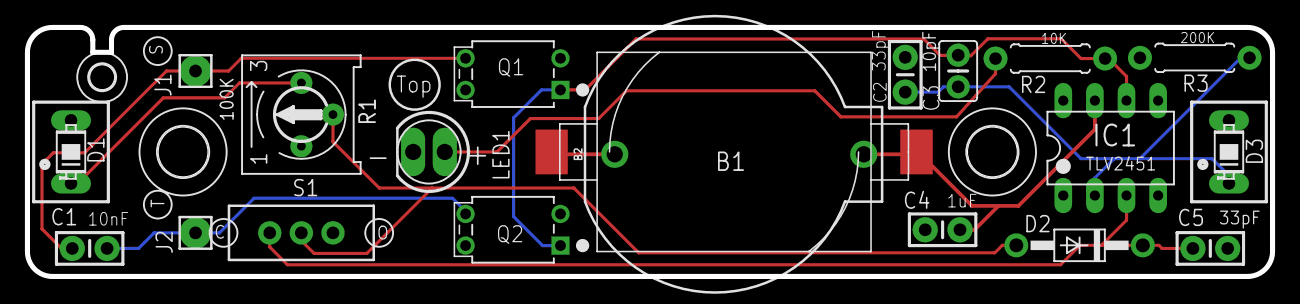
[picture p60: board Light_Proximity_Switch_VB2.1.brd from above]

Board: 2 copper layers, 100.0 x 20.0 mm, 23 parts (0 on the bottom side), 10 nets.

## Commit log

2020-05-06 Update Light_Proximity_Switch_Base_v1.0.stl
    Correct default orientation.
    [Light_Proximity_Switch_Base_v1.0.stl]
2020-05-06 Update 3D Print info
    Add 3d printing settings and orientation photo
2020-05-07 Correct folder naming
    [Light_Proximity_Switch_Base_v1.0.stl, Light_Proximity_Switch_Bottom_Case_v1.0.stl, Light_Proximity_Switch_Top_Case_v1.0.stl]
2020-05-07 Correct folder naming Pt 2
    [Light-Proximity-Switch-vB2.1.brd, Light-Proximity-Switch-vB2.1.sch, Light_Proximity_Switch_Base_v1.0.stl, Light_Proximity_Switch_Bottom_Case_v1.0.stl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]
2020-05-08 Added the PCB Fabrication Manual
2020-05-13 Added gerber files and board/schematics pdf files.
    [Light_Proximity_Switch_VB2.1.brd, Light_Proximity_Switch_VB2.1.sch]
2020-05-13 Added MMC PCB Fabrication Manual document.
2021-04-01 Added PCBWay gerbers
2021-07-02 Add Assembly Guide version
2025-04-04 Update to bottom case and renaming
    - Updated the bottom case model so improve printing of the unsupported screw holes.
    - Renamed stl files to remove versioning to make consistent with newer libraries
    - Added .STEP files in Design_Files folder
    [Light_Proximity_Switch_Base.step, Light_Proximity_Switch_Base.stl, Light_Proximity_Switch_Base_v1.0.stl, Light_Proximity_Switch_Bottom_Case.step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]
2026-01-17 Rename and reorganize documentation
    [Light_Proximity_Switch_BOM.csv, Light_Proximity_Switch_BOM.xlsx, Light_Proximity_Switch_BOM_v1.0.xlsx]
2026-01-17 Rename 3D printing file folder to match OpenAT Template
    3D_Printing -> 3D_Printing_Files
    [Light_Proximity_Switch_Base.stl, Light_Proximity_Switch_Bottom_Case.stl, Light_Proximity_Switch_Top_Case.stl]
2026-01-17 Reorganize PCB files
    [Light_Proximity_Switch_VB2.1.brd, Light_Proximity_Switch_VB2.1.sch]
2026-01-17 Reogranize CAD files
    [Light_Proximity_Switch_Base.step, Light_Proximity_Switch_Bottom_Case.step, Light_Proximity_Switch_Top_Case.step]
2026-01-17 Update Light Proximity Switch BOM components and pricing
    Revised the Bill of Materials for the Light Proximity Switch to update suppliers, manufacturers, part numbers, and pricing. Notable changes include switching the op-amp to MCP6231-E/P, updating sever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
    [Light_Proximity_Switch_BOM.csv, Light_Proximity_Switch_BOM.xlsx]
2026-04-08 Updated Base File
    Added the correct base file as the previous one was a accidental copy of the bottom case. This is relevant to Issue: ""Base" file is wrong #11"
    [Light_Proximity_Switch_Base.stl]

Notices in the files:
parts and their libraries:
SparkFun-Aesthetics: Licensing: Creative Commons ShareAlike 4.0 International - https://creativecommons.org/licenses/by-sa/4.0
